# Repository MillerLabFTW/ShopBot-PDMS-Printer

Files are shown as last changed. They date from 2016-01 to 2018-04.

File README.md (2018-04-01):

# ShopBot PDMS Printer

##### Modified ShopBot Desktop CNC for pneumatic 3D printing of PDMS elastomer
##### Miller Lab: Physiologic Systems Engineering and Advanced Materials
##### [millerlab.rice.edu](http://millerlab.rice.edu)
&nbsp;

The ability to 3D print with PDMS (polydimethylsiloxane) is extremely useful in the lab for constructing custom lab equipment and devices. We are 3D printing PDMS via a modified ShopBot desktop CNC system. The toolhead of the ShopBot was replaced with a simple syringe mount and PDMS is extruded through the syringe under air pressure.

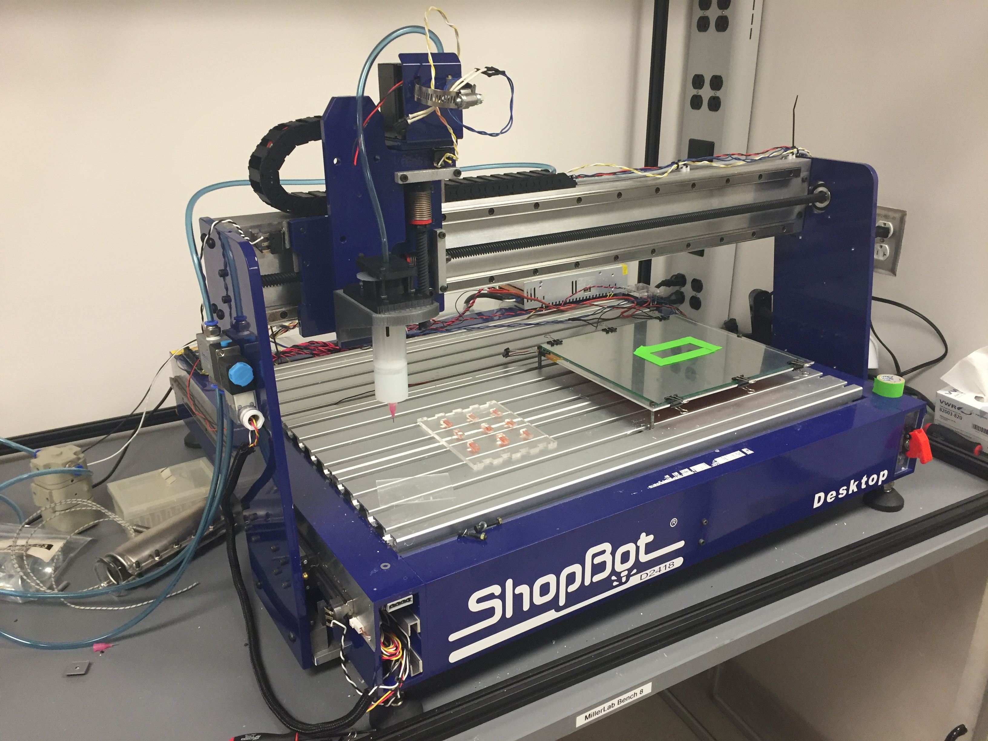
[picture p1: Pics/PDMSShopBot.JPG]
ShotBot pic


With an appropriate syringe mount, you can implement PDMS printing with this setup on any 3D printer running Marlin. We like the ShopBot for its robust construction, high-precision positioning, and large build area. 

### Documentation
This git repository includes:
- STL files for 3D printing syringe-mount for the ShopBot
- Current firmware (modified Marlin for pressure-driven extrusion)
- Cura configuration and G-code munging script for G-code creation and processing
- Wiring diagram for electronics configuration (based on RAMBo electronics)
- Instructions for 3D printing with PDMS
- Bill of materials

### Modifications to the ShopBot:
- Remove toolhead and replace with syringe holder (see Syringe Mount STLs)
- Remove motherboard and use RAMBo to signal onboard stepper drivers
- Install endstops 
- Install a build platform. We used extrusion pre-assembly nuts slipped in between the grooves of the ShopBot base to anchor an aluminum sheet for our build platform (spring-loaded for bed leveling). We print on glass, binder-clipped to the metal platform. 

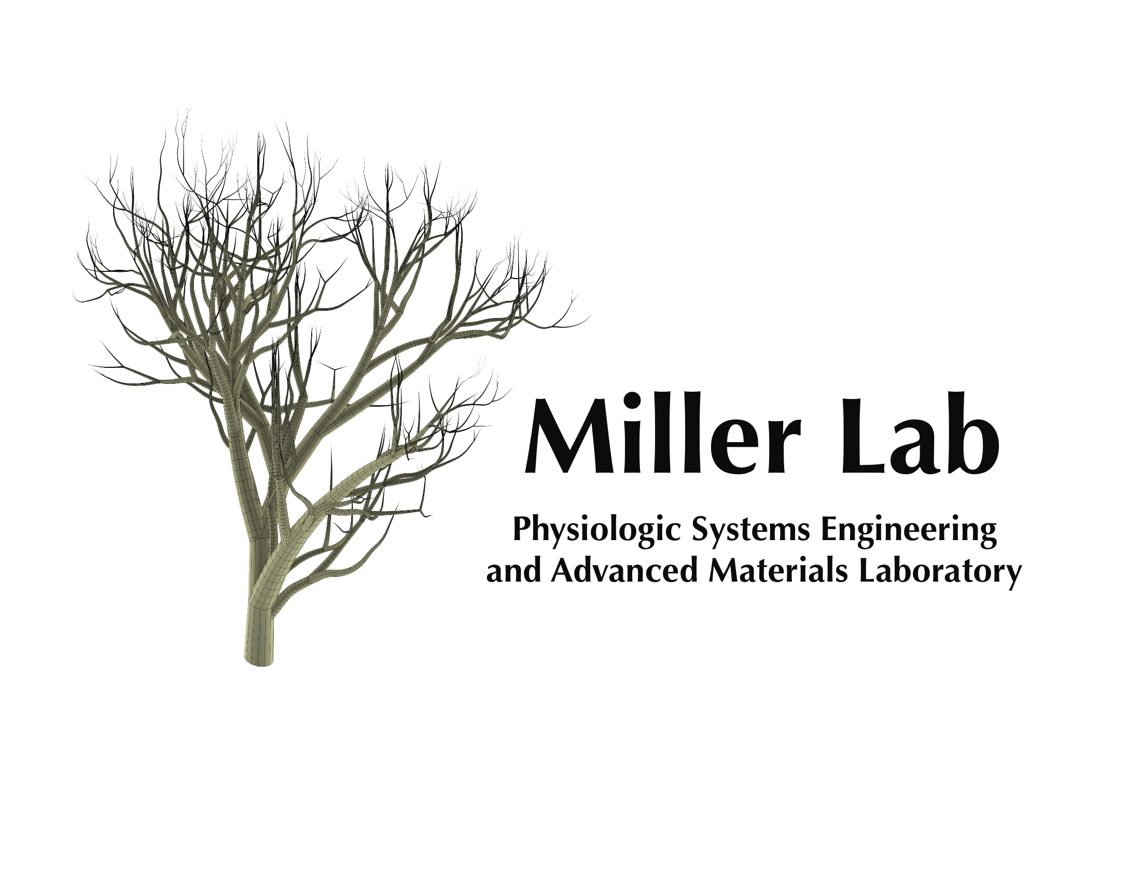
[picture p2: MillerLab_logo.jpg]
MillerLab logo


### Acknowledgements

3D printing of PDMS in this formulation was first demonstrated in Jennifer Lewis' lab at Harvard University:

D. B. Kolesky, R. L. Truby, A. S. Gladman, T. A. Busbee, K. A. Homan and J. A. Lewis, Adv. Mater., 2014, 26, 3124–3130.

Hat-tip to the [Lewis lab](http://lewisgroup.seas.harvard.edu/) for all the exciting 3D printing work that they do.

- Thanks to ShopBot for assistance modifying their desktop unit to be driven by RAMBo
- Thanks to Ultimachine for RAMBo support and assistance with electropneumatic transducers
- Thanks to the Marlin dev team and all the other open-source tools that support 3D printing

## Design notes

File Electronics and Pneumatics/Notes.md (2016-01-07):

# Pneumatics

Air should flow through the following series of components:

0. Tank or wall (~100 psi)
1. Regulator (~35 psi)
2. Electropneumatic transducer
3. Solenoid valve
4. Tubing to stoppered syringe

The transducer provides (some) pressure control while the solenoid valve rapidly applies and removes pressure to start and stop flow of PDMS. 

# Electronics

- It's necessary to convert PWM output from the RAMBo to a constant-voltage signal. We are using an "E2P" adapter from Ultimachine
- Wire the grounds together on the RAMBo and ShopBot power supplies to match ground planes
- A simple diagram is provided for connecting RAMBo motor ext pins to ShopBot stepper drivers via a 37-pin connector. We've also included pinout info for RAMBo and the ShopBot (thanks Shopbot!) for full specs.

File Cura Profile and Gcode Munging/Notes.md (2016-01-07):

# Notes for Gcode preparation

Gcode is generated using the Cura machine profile. Crucially, you need to select "Only follow mesh surface" under expert options in Cura so you only get single-layer walls in your gcode. 

The same effect can be achieved in Slic3r by setting zero top and bottom layers, zero infill, and 1 vertical shell. 

Note that depending on what needle you use on your syringe (we use [Nordson precision tips] (http://www.nordson.com/en/divisions/efd/products/dispense-tips/general-purpose-tips)), and what pressure you print at, the nozzle diameter will need to be changed. Our printing profile is based on printing with a 20GA 0.5" needle.

To print anything where the flow of PDMS needs to switch on and off (e.g. multiple parts next to each other, gaps between walls, etc), you need to add gcodes to open and close the solenoid valve. You can do this manually (see special gcodes below) or use a text munging tool we have provided. This simple script just looks through the original gcode for travel moves (G0 or G1 moves without an accompanying extrusion length) and turns off the pressure during these moves. 
The gcode munging script is supplied as a python script and and EXE.

## Special Gcodes for Pressure-driven extrusion

### M128 S## : Prime E2P
The electro-pneumatic transducer must be primed at the beginning of each print! This command requires a PWM value - we use M128 S110

### M127 : Close solenoid valve
Initiates flow of PDMS

### M129 : Vent solenoid
Stops flow of PDMS

# Start/end Gcode
#### The following Gcode should be used at the beginning/end of each file (should be part of the Cura profile already):

```
Start.gcode
G21        ;metric values
G90        ;absolute positioning
M128 S110; ;prime e2p
G28 X0 Y0  ;move X/Y to min endstops
G28 Z0     ;move Z to max endstops
G1 X350 Y30 F2000 ;move to print origin
G1 Z0.5 F2000 ;move the platform down 15mm
G92 X0 Y0 Z0.5 ;set current position to origin

End.gcode
M127 ;close solenoid
M129 ;vent e2p
G28 Z0 ;home Z max
G28 X0 Y0 ;home X/Y min
M84                         ;steppers off
G90                         ;absolute positioning
;{profile_string}

```

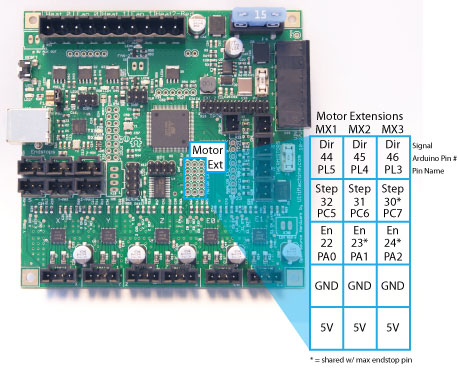
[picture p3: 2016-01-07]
Electronics and Pneumatics/RAMBo_motor_ext_pinout.jpg

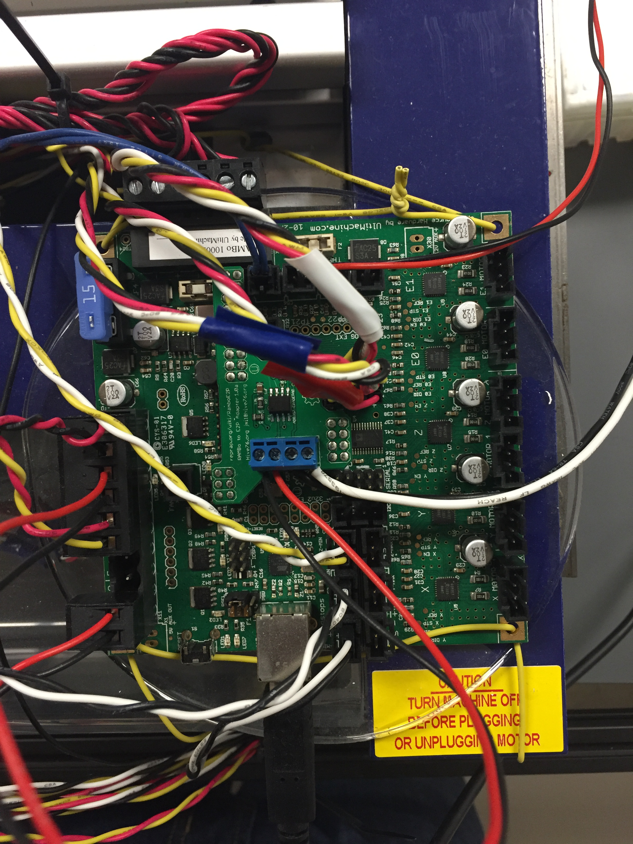
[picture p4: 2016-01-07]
Electronics and Pneumatics/Rambo_photo.JPG

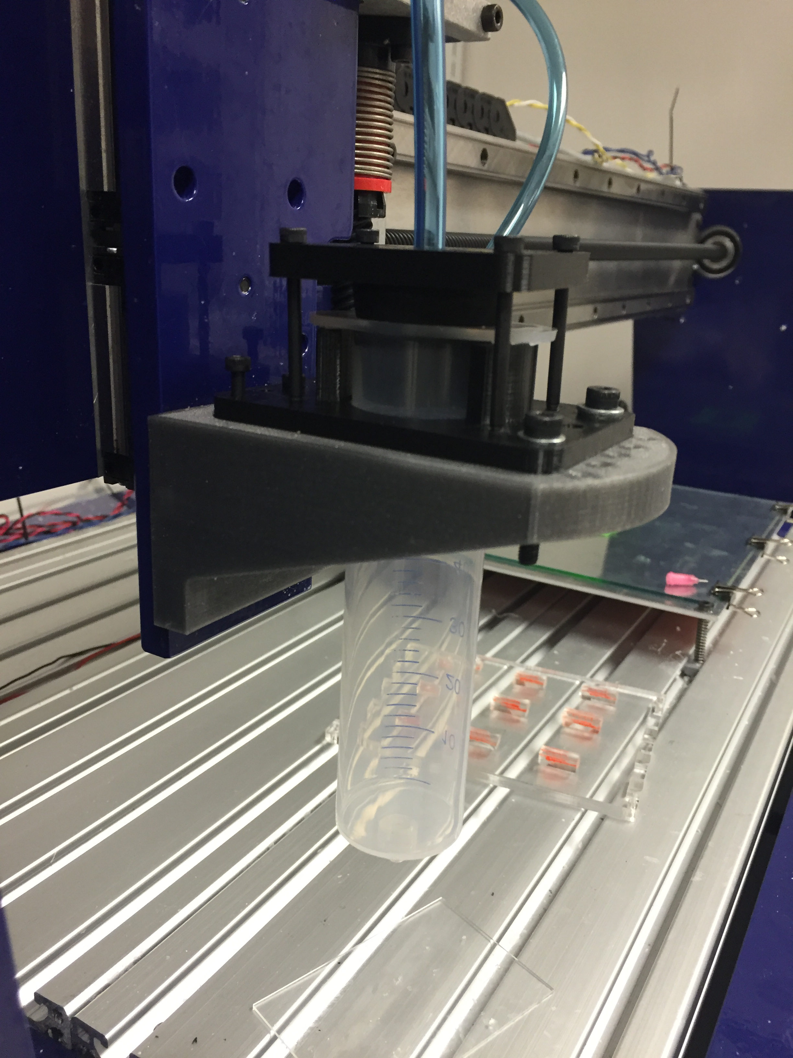
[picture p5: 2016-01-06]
Syringe Mount STLs/Syringe in clamp.JPG

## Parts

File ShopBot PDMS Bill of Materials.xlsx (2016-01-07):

 | PDMS ShopBot Bill of Materials
Quantity | Item | Vendor | Part No | Cost Per Item ($) | Total Cost ($) | Notes
1 | ShopBot Desktop D2418 | ShopBot | 10199 | 4995.00 | 4995.00
1 | Air pressure regulator | Cyberweld.com | 30-450-580 | 88.75 | 88.75 | Any pressure regulator is likely fine
1 | Electropneumatic Transducer | Omega | EP-211 | 340.00 | 340.00
1 | Solenoid valve | MettleAir | 3V210-08-DC12 | 24.38 | 24.38
1 | RAMBo | Ultimachine | UMRAMBOPAC13 | 170.00 | 170.00
1 | RAMBo E2P adapter | Ultimachine
1 | 12V 30A PSU | http://www.amazon.com/360w-Regulated-Switching-Power-Supply/dp/B0089VIBL2 |  | 25.65 | 25.65
1 | 37 pin connector | http://www.amazon.com/Connectors-Female-D-Sub-Solder-Connector/dp/B00RSXBQCI |  | 9.55 | 9.55 | Specifically for ShopBot motor control
1 | Endstop switches (x3) | http://www.amazon.com/Endstop-Microswitches-3D-Printer-CNC/dp/B00G2E6UZC?dpID=31eowOky14L&dpSrc=sims&preST=_AC_UL160_SR160%2C160_ |  | 6.45 | 6.45
 | Misc wire, pins, connectors
1 | Polyurethane tubing | MettleAir | PU 1/4-30CB | 22.30 | 22.30
5 | 1/4-N03 3/8" NPT thread push-to-connect straight connector | MettleAir | MTC 1/4-N03 | 1.56 | 7.80
1 | #6 rubber stopper | http://www.amazon.com/Rubber-Stopper--Size-6--Solid/dp/B006O2D6YU |  | 4.69 | 4.69 | Drill hole for tubing or buy pre-drilled
1 | Plastic 50mL (60mL) syringes w/ Luer Lock | Fisher Sci | 14-817-40 | 52.10 | 52.10
1 | 20 GA precision dispensing tips | Nordson | 7018178 | 23.83 | 23.83
 |  |  | Cost minus ShopBot |  | 775.50
 |  |  |  | Total cost | 5770.50

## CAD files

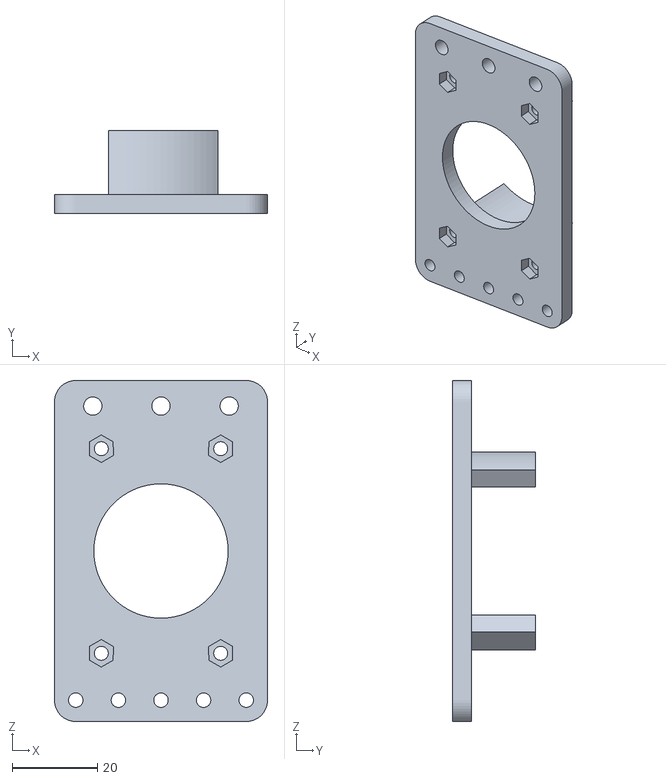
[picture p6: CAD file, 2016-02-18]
Syringe Mount STLs/50 mL syringe bottom.stl
50.0 x 19.5 x 80.0

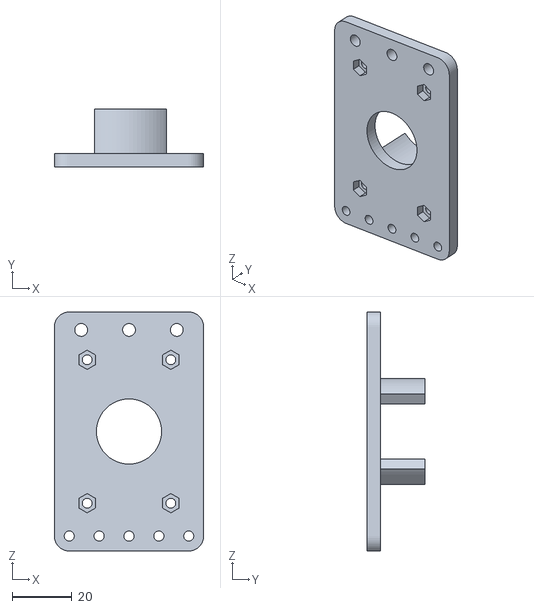
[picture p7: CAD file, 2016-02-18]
Syringe Mount STLs/20mL syringe bottom_v2.stl
50.0 x 19.5 x 80.0

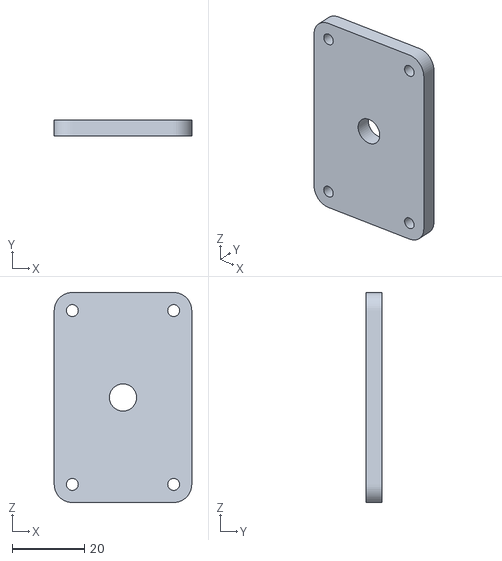
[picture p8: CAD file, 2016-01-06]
Syringe Mount STLs/Syringe_top_clamp.stl
38.0 x 4.50 x 58.0

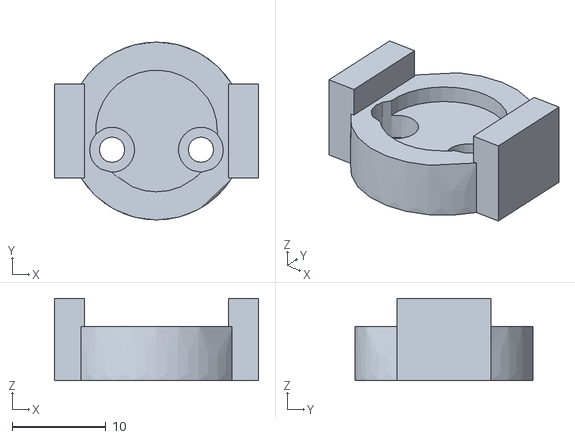
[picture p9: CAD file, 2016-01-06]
Syringe Mount STLs/EndstopHolderv3.stl
21.8 x 19.0 x 8.80

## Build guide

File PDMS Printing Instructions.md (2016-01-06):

# Printing with PDMS

### Materials Preparation

We are using non-flowing PDMS: [Dow Corning SE 1700] (http://www.dowcorning.com/applications/search/products/details.aspx?prod=01707116&type=PROD)
The mix of PDMS follows a 10 of base: 1 of catalyst. 

1. Grab a 60mL syringe. This is where we will deposit the materials. Remove the plunger at this time.
Use a luer lock stopper for the tip of the syringe. This will prevent materials from seeping out.
Place syringe in a cup on scale and tare to 0 g.  Use spatula to add base to syringe.  Avoid touching the material to the sides of the syringe, and try to get as much of the base towards the bottom of the syringe as possible.  (N.B. If too much of the base gets stuck on the sides of the syringe, you can centrifuge the syringe prior to adding the catalyst). 
2. Once the appropriate portions are added to the syringe, stir vigorously with a spatula for at least 5 minutes.
3. To rid the syringe of any air bubbles, we will now centrifuge the PDMS solution. Parafilm the top of the syringe to prevent any spills. You will likely need an special adapter for your centrifuge - we have a printed adapter for the 60mL syringe on our Allegra X-15R centrifuge and to counter weight! **Spin for 4 minutes at 2500CFM.**
4. Once the syringe is spun down and air bubbles are gone, remove the syringe from the centrifuge. If not, run it again until the mixture is bubble free. Decompress the bottom of the syringe if it was deformed in the centrifuge.
Grab the plunger for the syringe and cut it down at the first reinforced inner ring, this will be our piston for the air to press against. I like to drill a hole in the plunger so PDMS isn't lost while inserting the plunger.

5. Once the plunger is positioned well below the top of the syringe, you can now attach the syringe tip..
We can now load it onto the Shugabot with the proper adapter.
The 60mL syringe should fit rather snuggly into the holder. It will get a bit tighter around the area where the plunger is, apply a bit of force and it should clear it.
Seat the syringe all the way to the bottom, so that the flanges rest on the printer side walls.
Attach and secure the rubber stopper now. Tighten the four bolts around the stopper holder.
At this point you are ready to move over to the software side of things

### Slicing for PDMS Printing of Basic Profiles 

We will be using Cura to print with PDMS. The structures you can print at this time are only perimeters of objects, that is single/thin walled objects with little to no overhang. Further experimentation is needed for more complex geometries.

Open Cura and create a new machine. Go under “Machine” and choose “Add new machine” to do so.

A Cura profile has been created for use with 15ga needles (1.37mm ID). Feel free to change the various parameters such as speeds and layer thicknesses, just remember the nozzle size as a lot of parameters are based around it.

Go under the “Expert” option and go into “Open Expert Settings”. Make sure that “Only follow mesh contours” is checked. This is how we are achieving the single walled prints.

Once the settings are to your liking, go ahead and export the g-code. We will still need to modify the code physically.
Open the g-code file and find the start of the actual object. It is after the start sequence and is usually signified with a G0 move (a travel move). You need to add a M126 right before the G1 move that follows. This will allow the solenoid to open.
Since we are printing continuously so to speak, we simply need to have it turn of once it starts on the object. We also need to add a M127 to the last line of g-code for the object. This will close the solenoid.
**Note: This step (manual editing of gcode) is replaced by the gcode munging utility.**

Also ensure that the start and end gcode sequence is the following: (you can copy and paste if needed)

````
Start.gcode

;Sliced at: {day} {date} {time}
;Basic settings: Layer height: {layer_height} Walls: {wall_thickness} Fill: {fill_density}
;Print time: {print_time}
;Filament used: {filament_amount}m {filament_weight}g
;Filament cost: {filament_cost}
;M190 S{print_bed_temperature} ;Uncomment to add your own bed temperature line
;M109 S{print_temperature} ;Uncomment to add your own temperature line
G21        ;metric values
G90        ;absolute positioning
M128 S110; ;prime e2p
G28 X0 Y0  ;move X/Y to min endstops
G28 Z0     ;move Z to max endstops
G1 X350 Y30 F2000 ;move to print origin
G1 Z0.5 F2000 ;move the platform down 15mm
G92 X0 Y0 Z0.5 ;set current position to origin

End.gcode

M127 ;close solenoid
M129 ;vent e2p
G28 Z0 ;home Z max
G28 X0 Y0 ;home X/Y min
M84                         ;steppers off
G90                         ;absolute positioning
;{profile_string}
```

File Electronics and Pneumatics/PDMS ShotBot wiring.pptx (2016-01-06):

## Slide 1

Z endstop

Y endstop

X endstop

USB Connection to PC

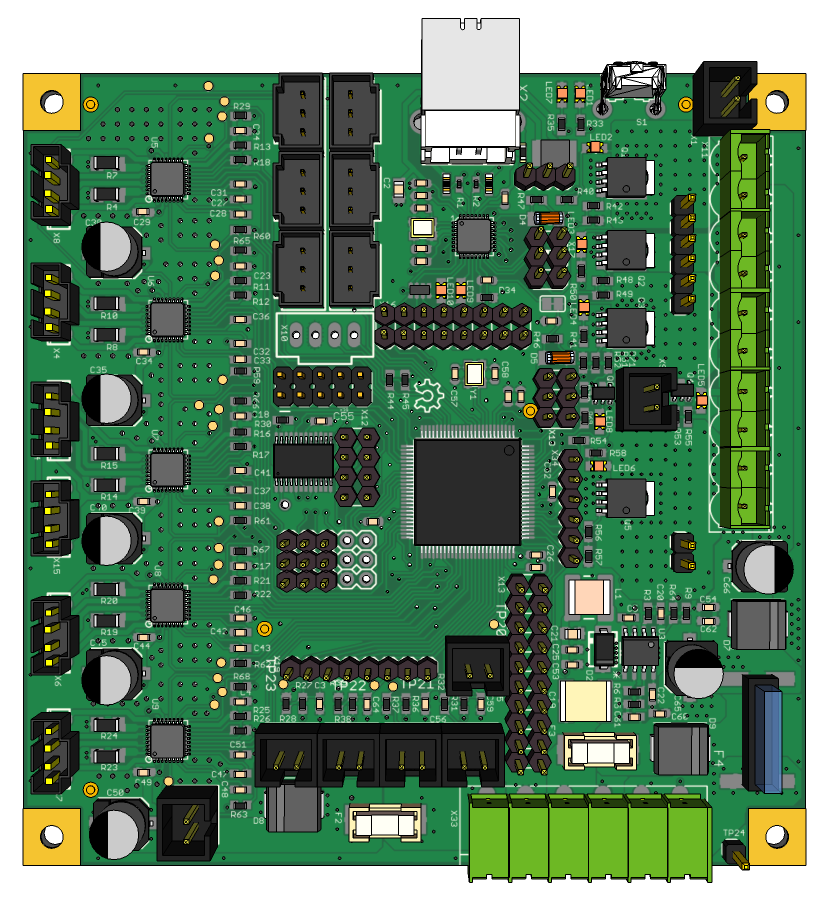
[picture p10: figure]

Solenoid Valve

PWM-Voltage Transducer

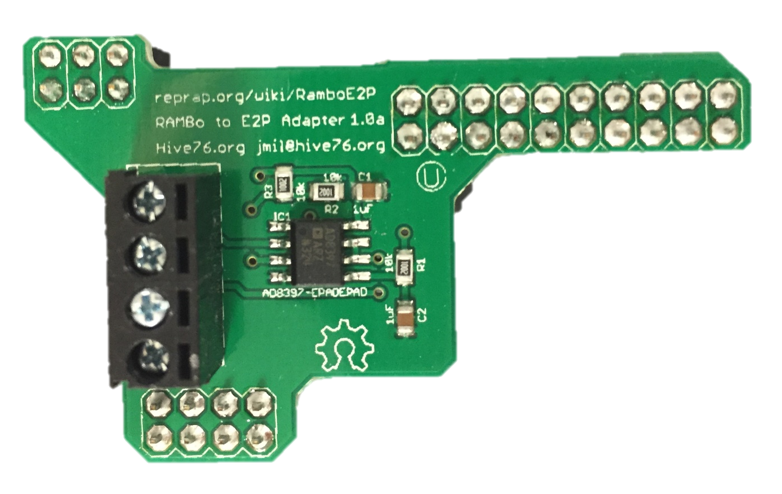
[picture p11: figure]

Electropneumatic (E/P) transducer

RAMBo v1.2

+ - + - + -

Optional heated bed

See zoomed in view of motor ext pins

RAMBo power supply: 12V DC; 30A

Important: RAMBo and ShopBot need common ground

ShopBot 48V built-in power supply

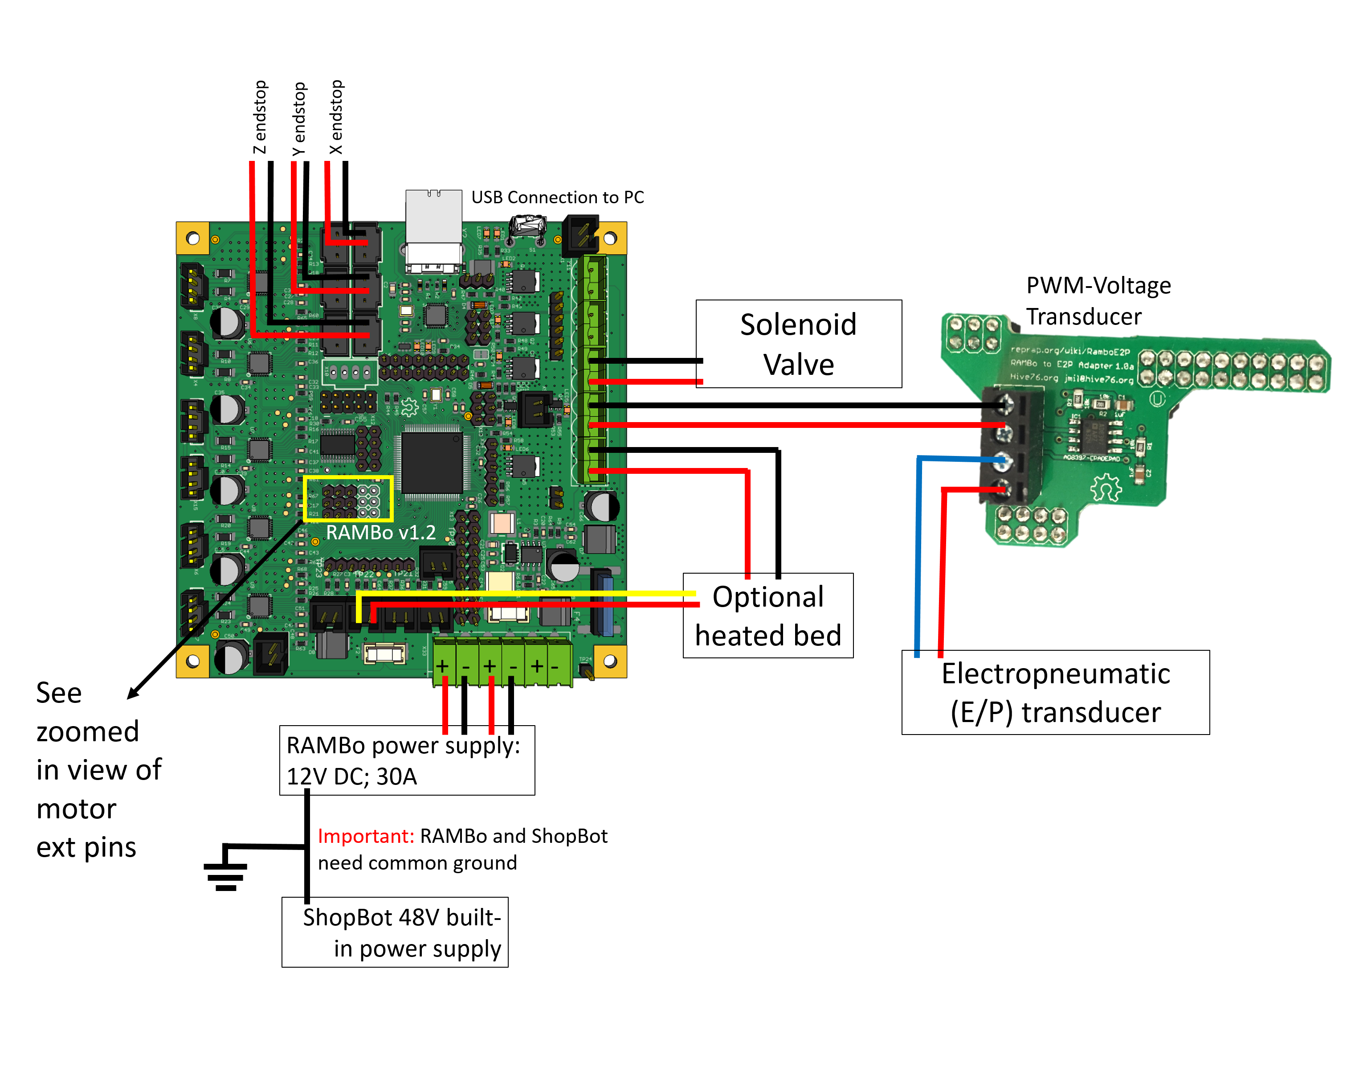
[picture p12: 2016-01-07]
Electronics and Pneumatics/Rambo_wiring_diagram.png

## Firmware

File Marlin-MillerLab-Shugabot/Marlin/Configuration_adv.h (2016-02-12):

#ifndef CONFIGURATION_ADV_H
#define CONFIGURATION_ADV_H

//===========================================================================
//=============================Thermal Settings  ============================
//===========================================================================

#ifdef BED_LIMIT_SWITCHING
  #define BED_HYSTERESIS 2 //only disable heating if T>target+BED_HYSTERESIS and enable heating if T>target-BED_HYSTERESIS
#endif
#define BED_CHECK_INTERVAL 5000 //ms between checks in bang-bang control

//// Heating sanity check:
// This waits for the watchperiod in milliseconds whenever an M104 or M109 increases the target temperature
// If the temperature has not increased at the end of that period, the target temperature is set to zero.
// It can be reset with another M104/M109. This check is also only triggered if the target temperature and the current temperature
//  differ by at least 2x WATCH_TEMP_INCREASE
//#define WATCH_TEMP_PERIOD 40000 //40 seconds
//#define WATCH_TEMP_INCREASE 10  //Heat up at least 10 degree in 20 seconds

#ifdef PIDTEMP
  // this adds an experimental additional term to the heatingpower, proportional to the extrusion speed.
  // if Kc is choosen well, the additional required power due to increased melting should be compensated.
  #define PID_ADD_EXTRUSION_RATE
  #ifdef PID_ADD_EXTRUSION_RATE
    #define  DEFAULT_Kc (1) //heatingpower=Kc*(e_speed)
  #endif
#endif


//automatic temperature: The hot end target temperature is calculated by all the buffered lines of gcode.
//The maximum buffered steps/sec of the extruder motor are called "se".
//You enter the autotemp mode by a M109 S<mintemp> T<maxtemp> F<factor>
// the target temperature is set to mintemp+factor*se[steps/sec] and limited by mintemp and maxtemp
// you exit the value by any M109 without F*
// Also, if the temperature is set to a value <mintemp, it is not changed by autotemp.
// on an ultimaker, some initial testing worked with M109 S215 B260 F1 in the start.gcode
#define AUTOTEMP
#ifdef AUTOTEMP
  #define AUTOTEMP_OLDWEIGHT 0.98
#endif

//Show Temperature ADC value
//The M105 command return, besides traditional information, the ADC value read from temperature sensors.
//#define SHOW_TEMP_ADC_VALUES

//  extruder run-out prevention.
//if the machine is idle, and the temperature over MINTEMP, every couple of SECONDS some filament is extruded
//#define EXTRUDER_RUNOUT_PREVENT
#define EXTRUDER_RUNOUT_MINTEMP 190
#define EXTRUDER_RUNOUT_SECONDS 30.
#define EXTRUDER_RUNOUT_ESTEPS 14. //mm filament
#define EXTRUDER_RUNOUT_SPEED 1500.  //extrusion speed
#define EXTRUDER_RUNOUT_EXTRUDE 100

//These defines help to calibrate the AD595 sensor in case you get wrong temperature measurements.
//The measured temperature is defined as "actualTemp = (measuredTemp * TEMP_SENSOR_AD595_GAIN) + TEMP_SENSOR_AD595_OFFSET"
#define TEMP_SENSOR_AD595_OFFSET 0.0
#define TEMP_SENSOR_AD595_GAIN   1.0

//This is for controlling a fan to cool down the stepper drivers
//it will turn on when any driver is enabled
//and turn off after the set amount of seconds from last driver being disabled again
#define CONTROLLERFAN_PIN -1 //Pin used for the fan to cool controller (-1 to disable)
#define CONTROLLERFAN_SECS 60 //How many seconds, after all motors were disabled, the fan should run
#define CONTROLLERFAN_SPEED 255  // == full speed

// When first starting the main fan, run it at full speed for the
// given number of milliseconds.  This gets the fan spinning reliably
// before setting a PWM value. (Does not work with software PWM for fan on Sanguinololu)
//#define FAN_KICKSTART_TIME 100

// Extruder cooling fans
// Configure fan pin outputs to automatically turn on/off when the associated
// extruder temperature is above/below EXTRUDER_AUTO_FAN_TEMPERATURE.
// Multiple extruders can be assigned to the same pin in which case
// the fan will turn on when any selected extruder is above the threshold.
#define EXTRUDER_0_AUTO_FAN_PIN   -1
#define EXTRUDER_1_AUTO_FAN_PIN   -1
#define EXTRUDER_2_AUTO_FAN_PIN   -1
#define EXTRUDER_AUTO_FAN_TEMPERATURE 50
#define EXTRUDER_AUTO_FAN_SPEED   255  // == full speed


//===========================================================================
//=============================Mechanical Settings===========================
//===========================================================================

#define ENDSTOPS_ONLY_FOR_HOMING // If defined the endstops will only be used for homing


//// AUTOSET LOCATIONS OF LIMIT SWITCHES
//// Added by ZetaPhoenix 09-15-2012
#ifdef MANUAL_HOME_POSITIONS  // Use manual limit switch locations
  #define X_HOME_POS MANUAL_X_HOME_POS
  #define Y_HOME_POS MANUAL_Y_HOME_POS
  #define Z_HOME_POS MANUAL_Z_HOME_POS
#else //Set min/max homing switch positions based upon homing direction and min/max travel limits
  //X axis
  #if X_HOME_DIR == -1
    #ifdef BED_CENTER_AT_0_0
      #define X_HOME_POS X_MAX_LENGTH * -0.5
    #else
      #define X_HOME_POS X_MIN_POS
    #endif //BED_CENTER_AT_0_0
  #else
    #ifdef BED_CENTER_AT_0_0
      #define X_HOME_POS X_MAX_LENGTH * 0.5
    #else
      #define X_HOME_POS X_MAX_POS
    #endif //BED_CENTER_AT_0_0
  #endif //X_HOME_DIR == -1

  //Y axis
  #if Y_HOME_DIR == -1
    #ifdef BED_CENTER_AT_0_0
      #define Y_HOME_POS Y_MAX_LENGTH * -0.5
    #else
      #define Y_HOME_POS Y_MIN_POS
    #endif //BED_CENTER_AT_0_0
  #else
    #ifdef BED_CENTER_AT_0_0
      #define Y_HOME_POS Y_MAX_LENGTH * 0.5
    #else
      #define Y_HOME_POS Y_MAX_POS
    #endif //BED_CENTER_AT_0_0
  #endif //Y_HOME_DIR == -1

  // Z axis
  #if Z_HOME_DIR == -1 //BED_CENTER_AT_0_0 not used
    #define Z_HOME_POS Z_MIN_POS
  #else
    #define Z_HOME_POS Z_MAX_POS
  #endif //Z_HOME_DIR == -1
#endif //End auto min/max positions
//END AUTOSET LOCATIONS OF LIMIT SWITCHES -ZP


//#define Z_LATE_ENABLE // Enable Z the last moment. Needed if your Z driver overheats.

// A single Z stepper driver is usually used to drive 2 stepper motors.
// Uncomment this define to utilize a separate stepper driver for each Z axis motor.
// Only a few motherboards support this, like RAMPS, which have dual extruder support (the 2nd, often unused, extruder driver is used
// to control the 2nd Z axis stepper motor). The pins are currently only defined for a RAMPS motherboards.
// On a RAMPS (or other 5 driver) motherboard, using this feature will limit you to using 1 extruder.
//#define Z_DUAL_STEPPER_DRIVERS

#ifdef Z_DUAL_STEPPER_DRIVERS
  #undef EXTRUDERS
  #define EXTRUDERS 1
#endif

// Same again but for Y Axis.
//#define Y_DUAL_STEPPER_DRIVERS

// Define if the two Y drives need to rotate in opposite directions
#define INVERT_Y2_VS_Y_DIR true

#ifdef Y_DUAL_STEPPER_DRIVERS
  #undef EXTRUDERS
  #define EXTRUDERS 1
#endif

#if defined (Z_DUAL_STEPPER_DRIVERS) && defined (Y_DUAL_STEPPER_DRIVERS)
  #error "You cannot have dual drivers for both Y and Z"
#endif

// Enable this for dual x-carriage printers.
// A dual x-carriage design has the advantage that the inactive extruder can be parked which
// prevents hot-end ooze contaminating the print. It also reduces the weight of each x-carriage
// allowing faster printing speeds.
//#define DUAL_X_CARRIAGE
#ifdef DUAL_X_CARRIAGE
// Configuration for second X-carriage
// Note: the first x-carriage is defined as the x-carriage which homes to the minimum endstop;
// the second x-carriage always homes to the maximum endstop.
#define X2_MIN_POS 80     // set minimum to ensure second x-carriage doesn't hit the parked first X-carriage
#define X2_MAX_POS 353    // set maximum to the distance between toolheads when both heads are homed
#define X2_HOME_DIR 1     // the second X-carriage always homes to the maximum endstop position
#define X2_HOME_POS X2_MAX_POS // default home position is the maximum carriage position
    // However: In this mode the EXTRUDER_OFFSET_X value for the second extruder provides a software
    // override for X2_HOME_POS. This also allow recalibration of the distance between the two endstops
    // without modifying the firmware (through the "M218 T1 X???" command).
    // Remember: you should set the second extruder x-offset to 0 in your slicer.

// Pins for second x-carriage stepper driver (defined here to avoid further complicating pins.h)
#define X2_ENABLE_PIN 29
#define X2_STEP_PIN 25
#define X2_DIR_PIN 23

// There are a few selectable movement modes for dual x-carriages using M605 S<mode>
//    Mode 0: Full control. The slicer has full control over both x-carriages and can achieve optimal travel results
//                           as long as it supports dual x-carriages. (M605 S0)
//    Mode 1: Auto-park mode. The firmware will automatically park and unpark the x-carriages on tool changes so
//                           that additional slicer support is not required. (M605 S1)
//    Mode 2: Duplication mode. The firmware will transparently make the second x-carriage and extruder copy all
//                           actions of the first x-carriage. This allows the printer to print 2 arbitrary items at
//                           once. (2nd extruder x offset and temp offset are set using: M605 S2 [Xnnn] [Rmmm])

// This is the default power-up mode which can be later using M605.
#define DEFAULT_DUAL_X_CARRIAGE_MODE 0

// As the x-carriages are independent we can now account for any relative Z offset
#define EXTRUDER1_Z_OFFSET 0.0           // z offset relative to extruder 0

// Default settings in "Auto-park Mode"
#define TOOLCHANGE_PARK_ZLIFT   0.2      // the distance to raise Z axis when parking an extruder
#define TOOLCHANGE_UNPARK_ZLIFT 1        // the distance to raise Z axis when unparking an extruder

// Default x offset in duplication mode (typically set to half print bed width)
#define DEFAULT_DUPLICATION_X_OFFSET 100

#endif //DUAL_X_CARRIAGE

//homing hits the endstop, then retracts by this distance, before it tries to slowly bump again:
#define X_HOME_RETRACT_MM 5
#define Y_HOME_RETRACT_MM 5
#define Z_HOME_RETRACT_MM 1
//#define QUICK_HOME  //if this is defined, if both x and y are to be homed, a diagonal move will be performed initially.

#define AXIS_RELATIVE_MODES {false, false, false, false}

#define MAX_STEP_FREQUENCY 40000 // Max step frequency for Ultimaker (5000 pps / half step)

//By default pololu step drivers require an active high signal. However, some high power drivers require an active low signal as step.
#define INVERT_X_STEP_PIN false
#define INVERT_Y_STEP_PIN false
#define INVERT_Z_STEP_PIN false
#define INVERT_E_STEP_PIN false

//default stepper release if idle
#define DEFAULT_STEPPER_DEACTIVE_TIME 60

#define DEFAULT_MINIMUMFEEDRATE       0.0     // minimum feedrate
#define DEFAULT_MINTRAVELFEEDRATE     0.0

// Feedrates for manual moves along X, Y, Z, E from panel
#ifdef ULTIPANEL
#define MANUAL_FEEDRATE {50*60, 50*60, 4*60, 60}  // set the speeds for manual moves (mm/min)
#endif

// minimum time in microseconds that a movement needs to take if the buffer is emptied.
#define DEFAULT_MINSEGMENTTIME        20000

// If defined the movements slow down when the look ahead buffer is only half full
#define SLOWDOWN

// Frequency limit
// See nophead's blog for more info
// Not working O
//#define XY_FREQUENCY_LIMIT  15

// Minimum planner junction speed. Sets the default minimum speed the planner plans for at the end
// of the buffer and all stops. This should not be much greater than zero and should only be changed
// if unwanted behavior is observed on a user's machine when running at very slow speeds.
#define MINIMUM_PLANNER_SPEED 0.05// (mm/sec)

// MS1 MS2 Stepper Driver Microstepping mode table
#define MICROSTEP1 LOW,LOW
#define MICROSTEP2 HIGH,LOW
#define MICROSTEP4 LOW,HIGH
#define MICROSTEP8 HIGH,HIGH
#define MICROSTEP16 HIGH,HIGH

// Microstep setting (Only functional when stepper driver microstep pins are connected to MCU.
#define MICROSTEP_MODES {1,1,1,1} // [1,2,4,8,16]
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

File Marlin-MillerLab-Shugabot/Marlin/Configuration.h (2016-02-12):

#ifndef CONFIGURATION_H
#define CONFIGURATION_H

// This configuration file contains the basic settings.
// Advanced settings can be found in Configuration_adv.h
// BASIC SETTINGS: select your board type, temperature sensor type, axis scaling, and endstop configuration

//===========================================================================
//============================= DELTA Printer ===============================
//===========================================================================
// For a Delta printer rplace the configuration files wilth the files in the
// example_configurations/delta directory.
//

// User-specified version info of this build to display in [Pronterface, etc] terminal window during
// startup. Implementation of an idea by Prof Braino to inform user that any changes made to this
// build by the user have been successfully uploaded into firmware.
#define STRING_VERSION_CONFIG_H __DATE__ " " __TIME__ // build date and time
#define STRING_CONFIG_H_AUTHOR "(ata, ShugaBot)" // Who made the changes.

// SERIAL_PORT selects which serial port should be used for communication with the host.
// This allows the connection of wireless adapters (for instance) to non-default port pins.
// Serial port 0 is still used by the Arduino bootloader regardless of this setting.
#define SERIAL_PORT 0

// This determines the communication speed of the printer
// This determines the communication speed of the printer
#define BAUDRATE 115200

// This enables the serial port associated to the Bluetooth interface
//#define BTENABLED              // Enable BT interface on AT90USB devices


//// The following define selects which electronics board you have. Please choose the one that matches your setup
// 10 = Gen7 custom (Alfons3 Version) "https://github.com/Alfons3/Generation_7_Electronics"
// 11 = Gen7 v1.1, v1.2 = 11
// 12 = Gen7 v1.3
// 13 = Gen7 v1.4
// 2  = Cheaptronic v1.0
// 20 = Sethi 3D_1
// 3  = MEGA/RAMPS up to 1.2 = 3
// 33 = RAMPS 1.3 / 1.4 (Power outputs: Extruder, Fan, Bed)
// 34 = RAMPS 1.3 / 1.4 (Power outputs: Extruder0, Extruder1, Bed)
// 35 = RAMPS 1.3 / 1.4 (Power outputs: Extruder, Fan, Fan)
// 4  = Duemilanove w/ ATMega328P pin assignment
// 5  = Gen6
// 51 = Gen6 deluxe
// 6  = Sanguinololu < 1.2
// 62 = Sanguinololu 1.2 and above
// 63 = Melzi
// 64 = STB V1.1
// 65 = Azteeg X1
// 66 = Melzi with ATmega1284 (MaKr3d version)
// 67 = Azteeg X3
// 68 = Azteeg X3 Pro
// 7  = Ultimaker
// 71 = Ultimaker (Older electronics. Pre 1.5.4. This is rare)
// 77 = 3Drag Controller
// 8  = Teensylu
// 80 = Rumba
// 81 = Printrboard (AT90USB1286)
// 82 = Brainwave (AT90USB646)
// 83 = SAV Mk-I (AT90USB1286)
// 9  = Gen3+
// 70 = Megatronics
// 701= Megatronics v2.0
// 702= Minitronics v1.0
// 90 = Alpha OMCA board
// 91 = Final OMCA board
// 301 = Rambo
// 21 = Elefu Ra Board (v3)

#ifndef MOTHERBOARD
#define MOTHERBOARD 301
#endif

// Define this to set a custom name for your generic Mendel,
// #define CUSTOM_MENDEL_NAME "This Mendel"
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

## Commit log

2016-01-06 Added 1st draft of most content
    [EndstopHolderv3.stl, Menu Plans.xlsx, Syringe_bottom_clamp.stl, Syringe_top_clamp.stl]
2016-01-06 Add tighter syringe holder
    [Syringe_bottom_clamp_tighter.stl]
2016-01-06 Updated wiring
    [ShopBot PDMS Bill of Materials.xlsx]
2016-01-07 Wiring diagrams quasi-complete
2016-01-07 Bill of Materials added
    [ShopBot PDMS Bill of Materials.xlsx]
2016-02-12 Corrected firmware
    [Menu Plans.xlsx]
2016-02-18 Add 20mL syringe mount
    [20mL syringe bottom_v2.stl, 50 mL syringe bottom.stl, Syringe_bottom_clamp.stl, Syringe_bottom_clamp_tighter.stl]
